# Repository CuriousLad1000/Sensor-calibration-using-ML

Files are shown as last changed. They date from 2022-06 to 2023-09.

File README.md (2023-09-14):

# Sensor calibration using Machine Learning

## Introduction

This repository presents one of the projects I built during the start of
the COVID-19 pandemic when there was a severe shortage of medical
equipment. Even something simple as a thermometer was either not
available or too costly to purchase. In this project, I used some
consumer-grade temperature sensors and calibrated them to provide
medical-grade precision and accuracy.

## Project Objective

The objective is to calibrate a commonly available temperature sensor to
provide medical grade accuracy. The sensor is calibrated by taking
readings from multiple medical grade thermometers as a benchmark and
then averaging them out.

The reading taken from thermometer and the sensor being calibrated are
then fit to a regression model to increase sensor's accuracy.

The model is then uploaded to the controller and after interfacing with
sensors and peripherals required, it produces accurate results under
calibrated range of a clinical thermometer (94-108 degrees F).

*Full list of features and capabilities are listed in a separate section below.*

## Hardware used

-   Arduino nano/pro min

-   3D printer casing for the temperature gun

-   Bright OLED display

-   battery

-   Laser pointer

-   Contactless Temperature sensor

-   Custom-built calibration heat bed

-   Clinical thermometers

-   Precision temperature sensors for heat-bed and reference

## Software used

-   Arduino IDE (C/C++ Programming)

-   Excel for data collection and regression model

-   GIMP for UI designing

-   Eagle for PCB designing

-   Fritzing for prototyping wiring diagram

## Features offered

-   Calibrated contactless temperature sensor.

-   Power-saving mode.

-   Inbuilt rechargeable batteries.

-   Temperature range similar to clinical thermometer.

-   Bright OLED display with easy-to-read readouts.

## Device pics

**Device**

<br/>

<p align="Center">
  
</p>

<br/>
<br/>

**Calibration setup <i>(gotta work with whatever you have during pandemic... this is a makeshift Heatbed PID controlled)</i>**

<br/>

<p align="Center">
  
</p>

<br/>
<br/>

<br/>

<p align="Center">
  
</p>

<br/>
<br/>

**Circuit board**

<br/>

<p align="Center">
  
</p>

<br/>
<br/>

**Calibration process**

<br/>

<p align="Center">
  
</p>

<br/>
<br/>

**UI Testing**

<br/>

<p align="Center">
  
</p>

<br/>
<br/>

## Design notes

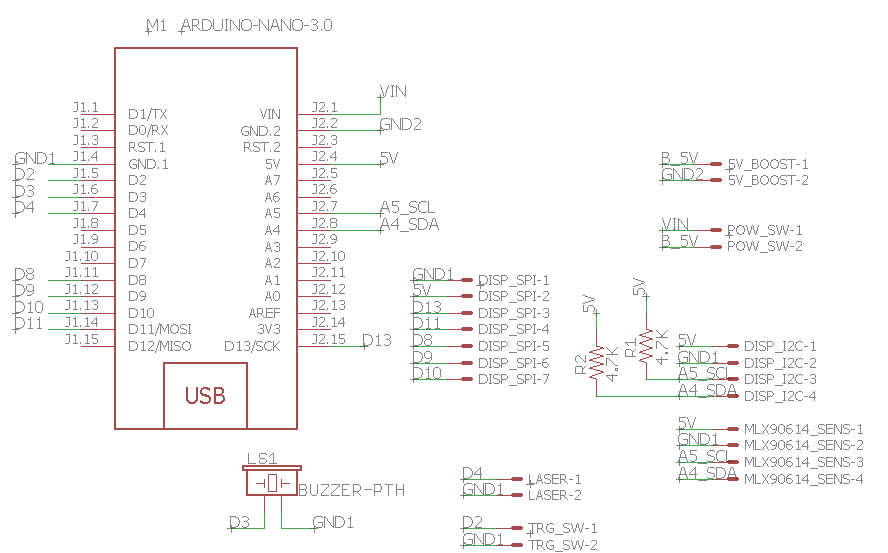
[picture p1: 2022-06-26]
Circuit Schematic/circuit schematic.png

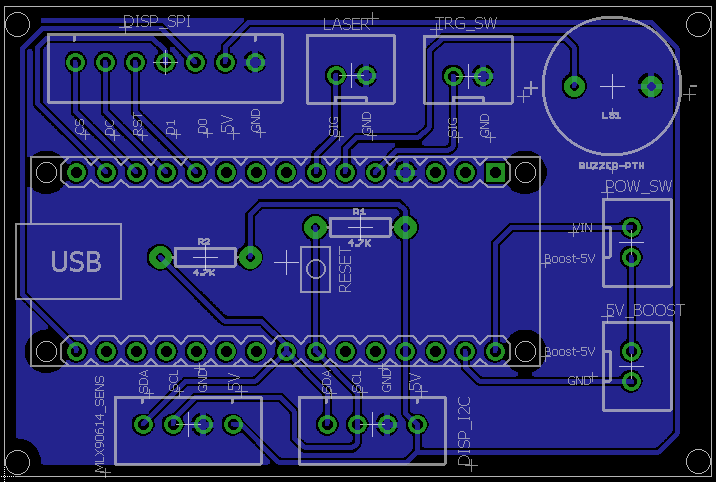
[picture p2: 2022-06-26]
Circuit Schematic/circuit board.png

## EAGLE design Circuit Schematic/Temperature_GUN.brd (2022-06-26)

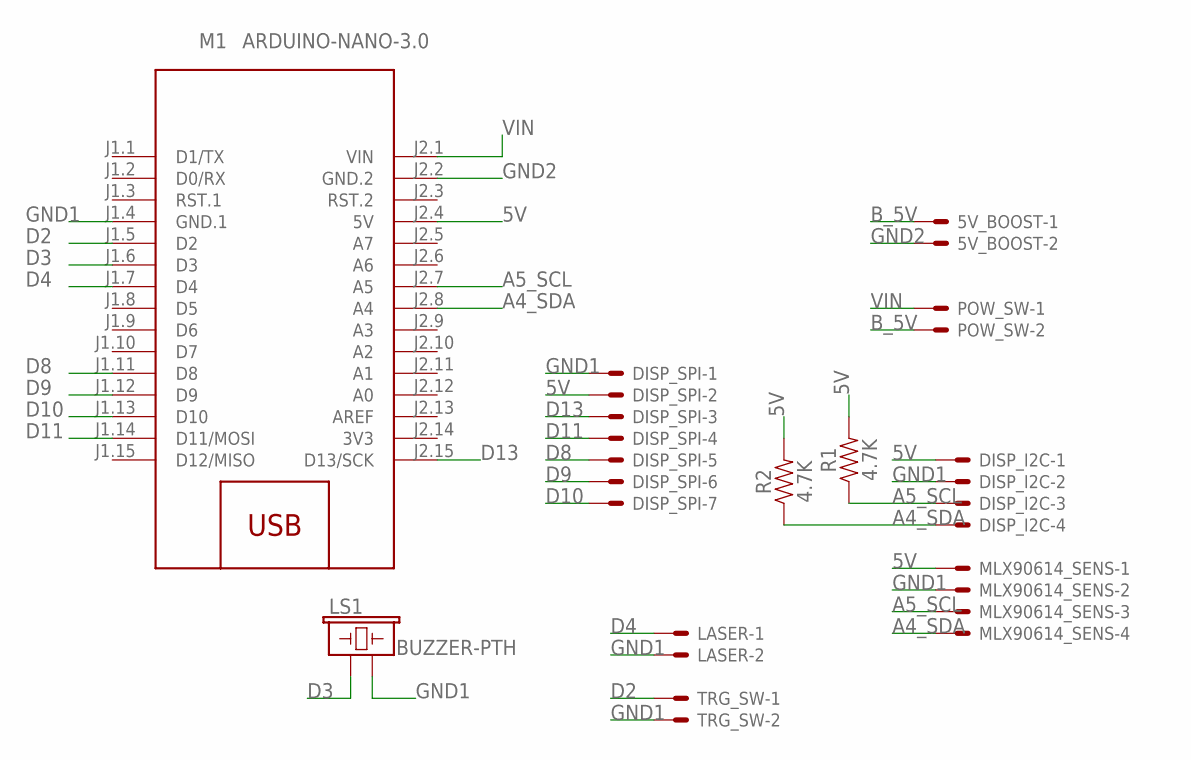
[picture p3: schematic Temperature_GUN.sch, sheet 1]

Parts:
5V_BOOST: JST-XH-02-PIN-ROUND-PAD; JST-XH-02-PACKAGE-ROUND-PAD
DISP_I2C: JST-XH-04-PIN-ROUND-PAD; JST-XH-04-PACKAGE-ROUND-PAD
DISP_SPI: JST-XH-07-PIN-ROUND-PAD; JST-XH-07-PACKAGE-ROUND-PAD
LASER: JST-XH-02-PIN-ROUND-PAD; JST-XH-02-PACKAGE-ROUND-PAD
LS1: BUZZER-PTH; BUZZER-12MM
M1: ARDUINO-NANO-3.0
MLX90614_SENS: JST-XH-04-PIN-ROUND-PAD; JST-XH-04-PACKAGE-ROUND-PAD
POW_SW: JST-XH-02-PIN-ROUND-PAD; JST-XH-02-PACKAGE-ROUND-PAD
R1, R2: 4.7K; AXIAL-0.3
TRG_SW: JST-XH-02-PIN-ROUND-PAD; JST-XH-02-PACKAGE-ROUND-PAD

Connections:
3V3: M1.J2.14 (3V3)
5V: DISP_I2C.1, DISP_SPI.2, M1.J2.4 (5V), MLX90614_SENS.1, R1.P$2 (2), R2.P$2 (2)
A4_SDA: DISP_I2C.4, M1.J2.8 (A4), MLX90614_SENS.4, R2.P$1 (1)
A5_SCL: DISP_I2C.3, M1.J2.7 (A5), MLX90614_SENS.3, R1.P$1 (1)
B_5V: 5V_BOOST.1, POW_SW.2
D2: M1.J1.5 (D2), TRG_SW.1
D3: LS1.+ (1), M1.J1.6 (D3)
D4: LASER.1, M1.J1.7 (D4)
D8: DISP_SPI.5, M1.J1.11 (D8)
D9: DISP_SPI.6, M1.J1.12 (D9)
D10: DISP_SPI.7, M1.J1.13 (D10)
D11: DISP_SPI.4, M1.J1.14 (D11/MOSI)
D13: DISP_SPI.3, M1.J2.15 (D13/SCK)
GND1: DISP_I2C.2, DISP_SPI.1, LASER.2, LS1.- (2), M1.J1.4 (GND.1), MLX90614_SENS.2, TRG_SW.2
GND2: 5V_BOOST.2, M1.J2.2 (GND.2)
VIN: M1.J2.1 (VIN), POW_SW.1

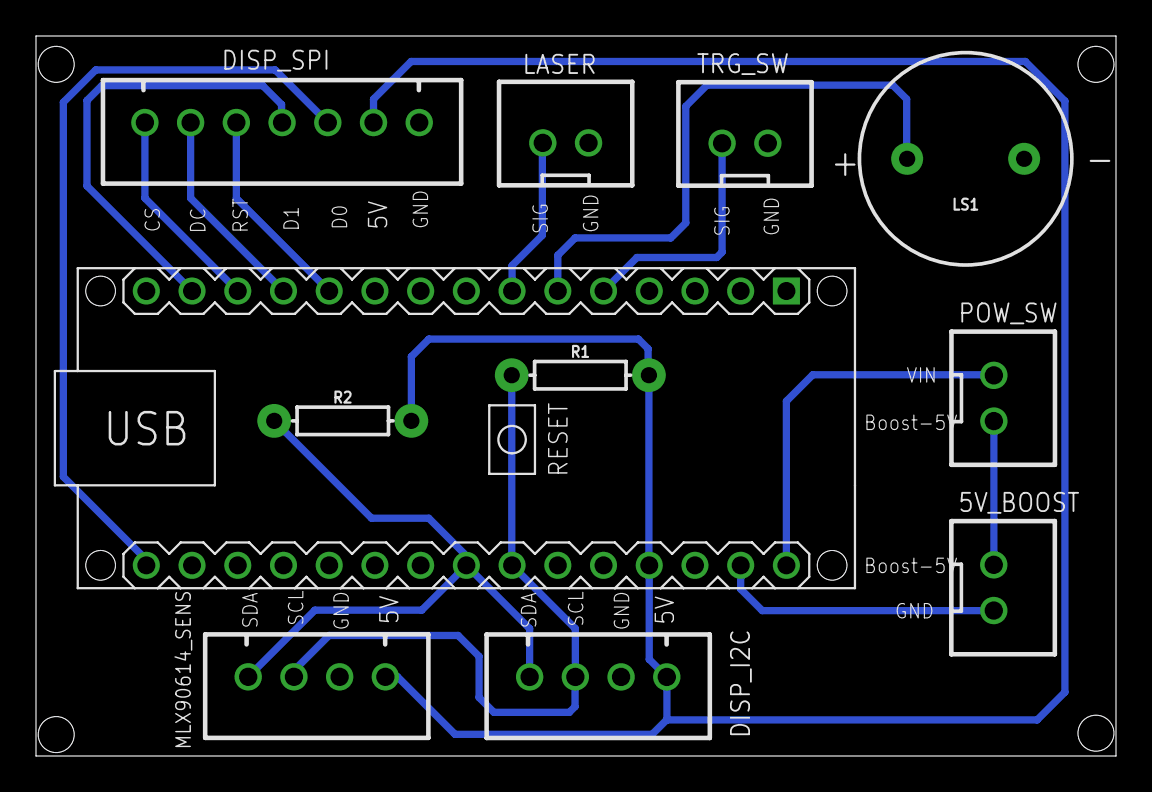
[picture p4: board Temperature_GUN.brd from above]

Board: 2 copper layers, 60.0 x 40.0 mm, 11 parts (0 on the bottom side), 15 nets.

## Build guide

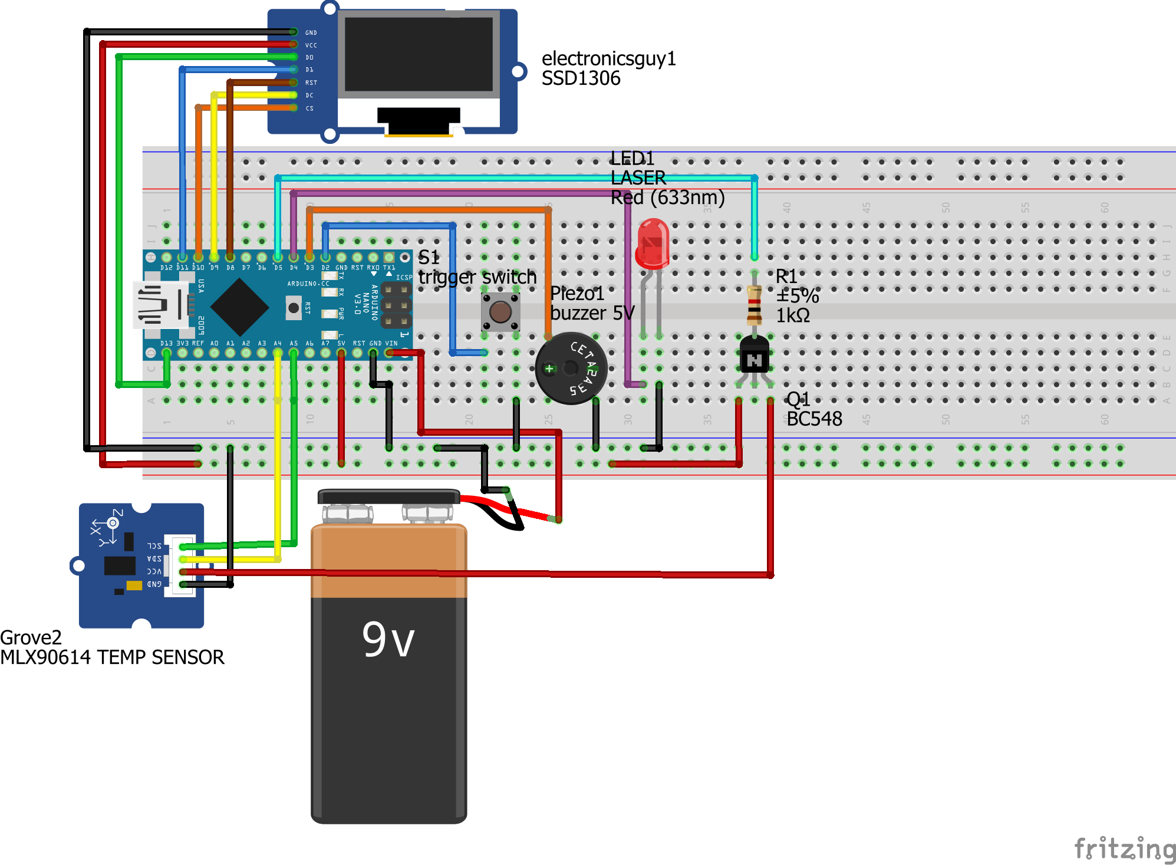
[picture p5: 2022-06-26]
Wiring Diagrams/Temperature_GUN_bb_v6.png

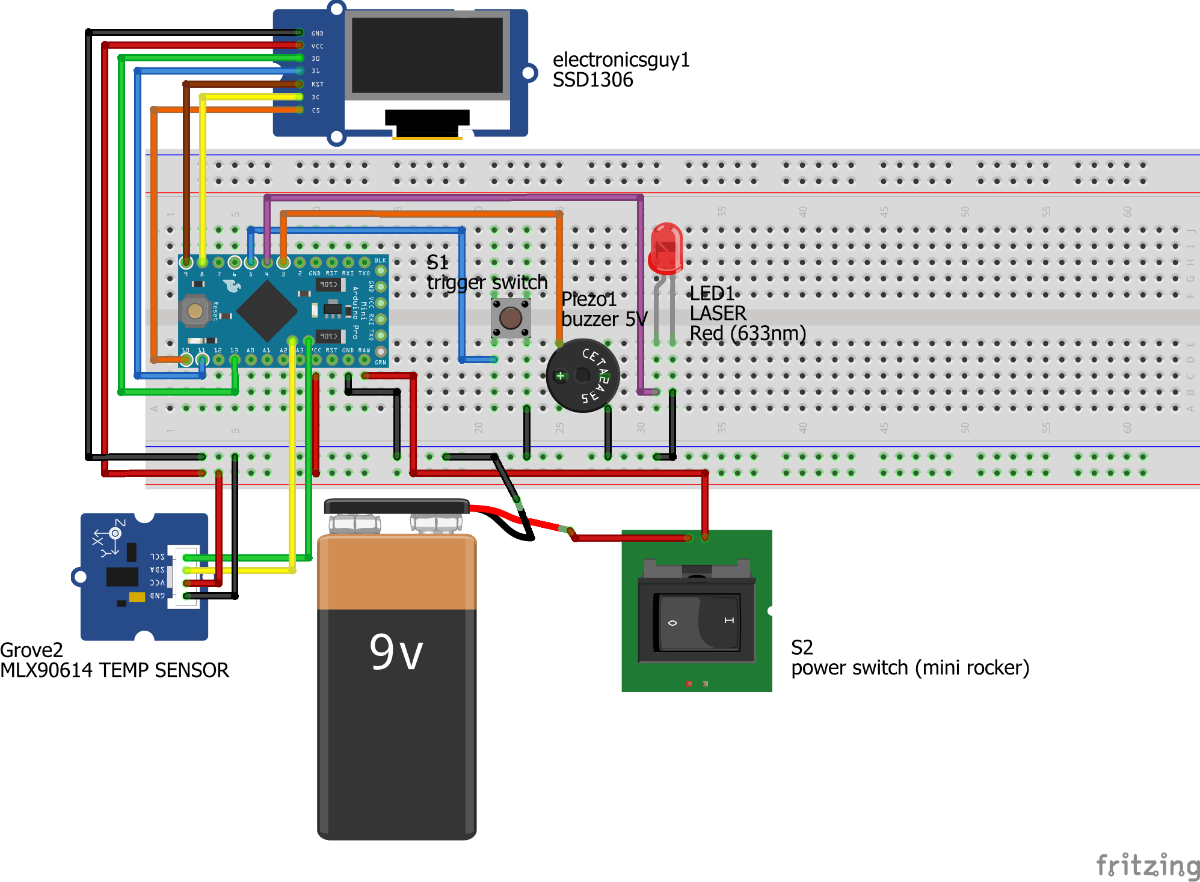
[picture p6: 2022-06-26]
Wiring Diagrams/Temperature_GUN_pro-mini.png

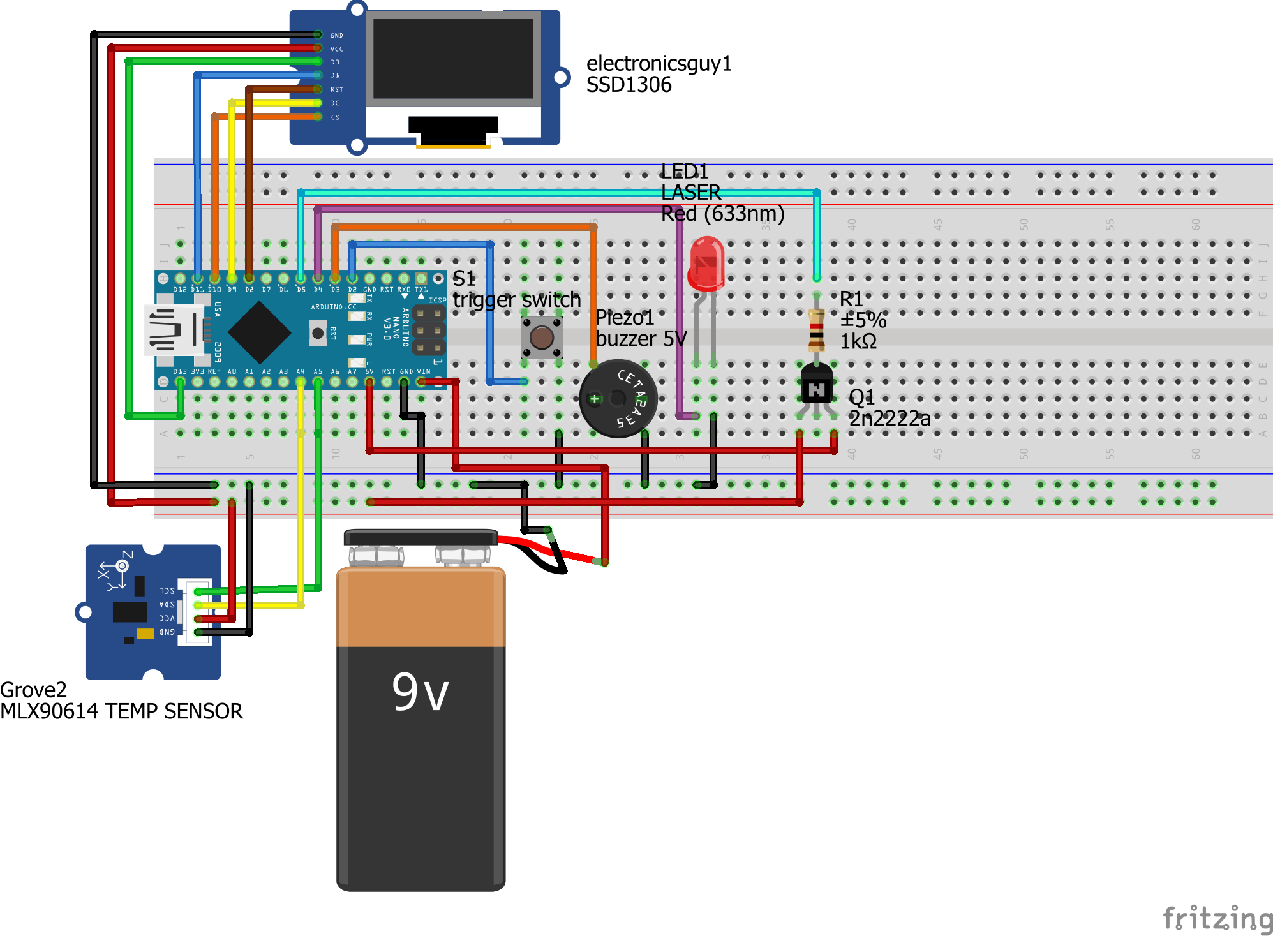
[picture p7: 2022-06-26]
Wiring Diagrams/Temperature_GUN_bb_SingleButton_V5.png

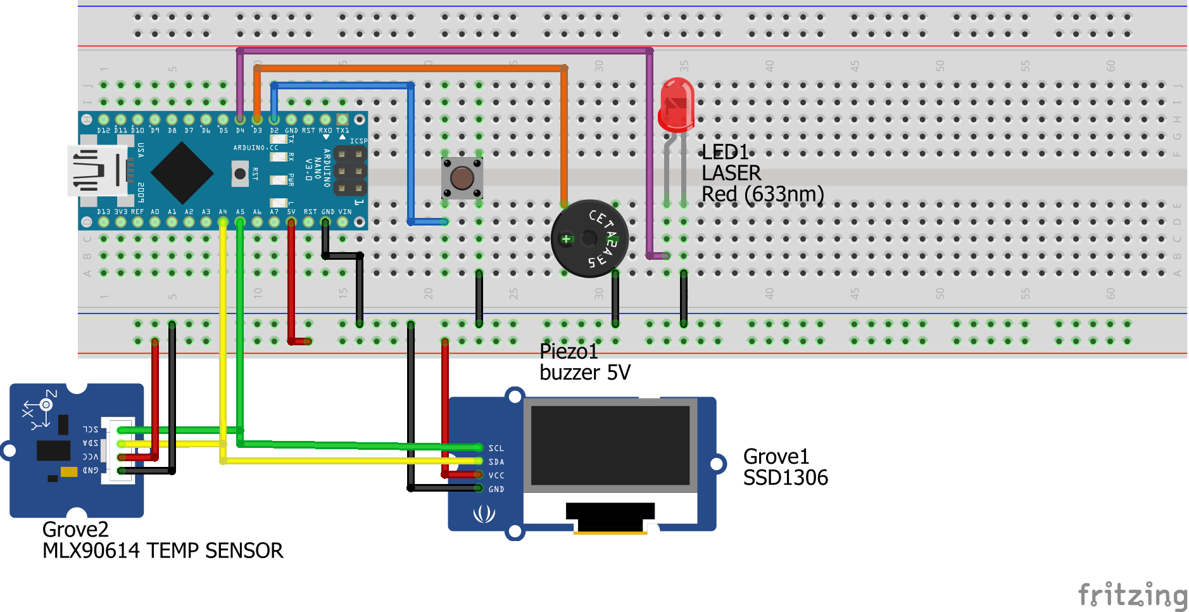
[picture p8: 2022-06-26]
Wiring Diagrams/Temperature_GUN_bb.png

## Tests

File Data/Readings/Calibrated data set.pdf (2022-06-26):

Reference Clinical Thermometer Readout (Y var.) | SET-AVERAGE | Average Regression
Calibrating contactless sensor Readout (2-3 cm) (X var.) | DIFF bw clinical and sensor | Regressed values Calibrating sensor (ŷ = 1.02751X -0.34754) | Diff between Clinical and Regressed Calibrating sensor
Read at (deg F) | Read at (deg F) | Read at (deg F) | Read at (deg F) | Read at (deg F)
94 | 91.57 | 2.43 | 93.74 | 0.26
94.4 | 92.59 | 1.81 | 94.79 | -0.39
94.8 | 93.03 | 1.77 | 95.24 | -0.44
95 | 93.14 | 1.86 | 95.35 | -0.35
95.4 | 93.35 | 2.05 | 95.57 | -0.17
95.8 | 93.59 | 2.21 | 95.81 | -0.01
96 | 93.94 | 2.06 | 96.18 | -0.18
96.4 | 94.20 | 2.20 | 96.45 | -0.05
96.8 | 94.67 | 2.13 | 96.93 | -0.13
97 | 94.65 | 2.35 | 96.90 | 0.10
97.4 | 95.00 | 2.40 | 97.26 | 0.14
97.8 | 95.24 | 2.56 | 97.51 | 0.29
98 | 95.68 | 2.32 | 97.96 | 0.04
98.2 | 95.84 | 2.36 | 98.13 | 0.07
98.4 | 96.08 | 2.32 | 98.38 | 0.02
98.6 | 96.19 | 2.41 | 98.49 | 0.11
98.8 | 96.42 | 2.38 | 98.72 | 0.08
99 | 96.58 | 2.42 | 98.89 | 0.11
99.2 | 96.80 | 2.40 | 99.11 | 0.09
99.4 | 97.04 | 2.36 | 99.37 | 0.03
99.6 | 97.31 | 2.29 | 99.64 | -0.04
99.8 | 97.53 | 2.27 | 99.87 | -0.07
100 | 97.60 | 2.40 | 99.94 | 0.06
100.2 | 97.83 | 2.37 | 100.18 | 0.02
100.4 | 97.93 | 2.47 | 100.28 | 0.12
100.6 | 98.12 | 2.48 | 100.48 | 0.12
100.8 | 98.35 | 2.45 | 100.71 | 0.09
101 | 98.60 | 2.40 | 100.96 | 0.04
101.2 | 98.69 | 2.51 | 101.06 | 0.14
101.4 | 99.05 | 2.35 | 101.43 | -0.03
101.6 | 99.28 | 2.32 | 101.67 | -0.07
101.8 | 99.23 | 2.57 | 101.62 | 0.18
102 | 99.47 | 2.53 | 101.86 | 0.14
102.2 | 99.65 | 2.55 | 102.04 | 0.16
102.4 | 99.85 | 2.55 | 102.25 | 0.15
102.6 | 100.28 | 2.32 | 102.69 | -0.09
102.8 | 100.44 | 2.36 | 102.85 | -0.05
103 | 100.63 | 2.37 | 103.05 | -0.05
103.4 | 100.89 | 2.51 | 103.32 | 0.08
103.8 | 101.14 | 2.66 | 103.58 | 0.22

104 | 101.47 | 2.53 | 103.91 | 0.09
104.4 | 102.02 | 2.38 | 104.48 | -0.08
104.8 | 102.26 | 2.54 | 104.72 | 0.08
105 | 102.55 | 2.45 | 105.02 | -0.02
105.4 | 102.85 | 2.55 | 105.33 | 0.07
105.8 | 103.29 | 2.51 | 105.78 | 0.02
106 | 103.51 | 2.49 | 106.01 | -0.01
106.4 | 104.05 | 2.35 | 106.56 | -0.16
106.8 | 104.27 | 2.53 | 106.79 | 0.01
107 | 104.54 | 2.46 | 107.07 | -0.07
107.4 | 105.03 | 2.37 | 107.57 | -0.17
107.8 | 105.50 | 2.30 | 108.05 | -0.25
108 | 105.66 | 2.34 | 108.22 | -0.22
AVERAGE OFFSET of | 2.36
ŷ = 1.02751X - 0.34754

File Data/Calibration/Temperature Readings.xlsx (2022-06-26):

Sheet: Sheet1
 | Reference Clinical Thermometer Readout | Temperature Gun Readout (2-3cm) | Temperature Difference (clinical and gun) | Lab Thermometer Readout | Lab Thermometer Readout | Temperature Difference (lab and clinical)
Count | Read at (deg F) | Read at (deg F) | Read at (deg F) | Read at (deg F) | Read at (deg C) | Read at (deg F)
0 | 94 | 89.01 | 4.99 | 93.2 | 34 | 0.8
1 | 94.2 | 88.68 | 5.52 | 93.2 | 34 | 1
2 | 94.4 | 88.83 | 5.57 | 93.2 | 34 | 1.2
3 | 94.6 | 88.86 | 5.74 | 93.2 | 34 | 1.4
4 | 94.8 | 88.73 | 6.07 | 93.2 | 34 | 1.6
5 | 95 | 88.92 | 6.08 | 93.2 | 34 | 1.8
6 | 95.2 | 88.94 | 6.26 | 93.2 | 34 | 2
7 | 95.4 | 89.33 | 6.07 | 93.2 | 34 | 2.2
8 | 95.6 | 89.2 | 6.4 | 93.2 | 34 | 2.4
9 | 95.8 | 89.01 | 6.79 | 93.2 | 34 | 2.6
10 | 96 | 89.08 | 6.92 | 93.2 | 34 | 2.8
11 | 96.2 | 88.79 | 7.41 | 93.2 | 34 | 3
12 | 96.4 | 88.4 | 8 | 93.2 | 34 | 3.2
13 | 96.6 | 88.9 | 7.7 | 93.2 | 34 | 3.4
14 | 96.8 | 88.25 | 8.55 | 93.2 | 34 | 3.6
15 | 97 | 89.01 | 7.99 | 93.2 | 34 | 3.8
16 | 97.2 | 88.57 | 8.63 | 93.2 | 34 | 4
17 | 97.4 | 88.83 | 8.57 | 93.2 | 34 | 4.2
18 | 97.6 | 89.4 | 8.2 | 93.2 | 34 | 4.4
19 | 97.8 | 89.12 | 8.68 | 93.2 | 34 | 4.6
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

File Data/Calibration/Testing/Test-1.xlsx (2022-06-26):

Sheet: Sheet2
Reference Clinical Thermometer Readout | Temperature Gun Readout(2-3cm) | Temperature Difference
Read at (deg F) | Read at (deg F) | Read at (deg F)
100.2 | 99.4 | 0.8
100.4 | 99.75 | 0.65
100.6 | 99.83 | 0.77
101.4 | 100.8 | 0.6
101.6 | 100.14 | 1.46
101.8 | 100.99 | 0.81
102 | 101.09 | 0.91
102.2 | 100.41 | 1.79
102.8 | 101.8 | 1
103 | 102.32 | 0.68
103.2 | 102.84 | 0.36
103.4 | 103.53 | -0.13
103.6 | 102.98 | 0.62
103.8 | 102.91 | 0.89
104 | 103.32 | 0.68
104.2 | 103.55 | 0.65
104.4 | 103.43 | 0.97
104.6 | 103.53 | 1.07
105 | 103.9 | 1.1
105.2 | 104.64 | 0.56
105.4 | 105.85 | -0.45
105.6 | 105.99 | -0.39
105.8 | 105.56 | 0.24
106.4 | 106.42 | -0.02
107.2 | 106.77 | 0.43
107.6 | 107.1 | 0.5
107.8 | 107.45 | 0.35
108 | 107.72 | 0.28
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

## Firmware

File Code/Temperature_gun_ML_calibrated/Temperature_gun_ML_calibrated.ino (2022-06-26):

#include <Arduino.h>
#include <U8g2lib.h>
#include <SparkFunMLX90614.h> // SparkFunMLX90614 Arduino library
#include <Wire.h>
//#include <movingAvg.h>



#define MSG_DEBUG
#define home_page_width 128
#define home_page_height 64

#define normal_tempF_max  99.5
#define mild_tempF_max    101


//#define MovReadings 10
#define avgReadings 8

//amb. temp >83 & < 91  avg offset 3.23

#define m1   1.02751
#define c1  -0.34754

//amb. temp >91  avg offset 3.23
#define m2   1.03983
#define c2  -0.66635

U8G2_SSD1306_128X64_NONAME_1_4W_HW_SPI u8g2(U8G2_R0, /* cs=*/ 10, /* dc=*/ 9, /* reset=*/ 8);

IRTherm therm; // Create an IRTherm object to interact with throughout
//movingAvg TEMP(MovReadings);

static const unsigned char splash_120x63_bits[] U8X8_PROGMEM = {
  //enter here splash screen .xbm code
};

static const unsigned char welcome_120x36_bits[] U8X8_PROGMEM = {
  //enter here welcome screen .xbm code
};

static const unsigned char cool_28x28_bits[] U8X8_PROGMEM = {
  0x00, 0x00, 0x00, 0x00, 0x00, 0x60, 0x00, 0x00, 0x00, 0x64, 0x02, 0x00,
  0x00, 0x68, 0x01, 0x00, 0x00, 0xf0, 0x00, 0x00, 0x40, 0x60, 0x20, 0x00,
  0x40, 0x60, 0x20, 0x00, 0x4c, 0x60, 0x20, 0x03, 0x78, 0x60, 0xe0, 0x01,
  0xe0, 0x60, 0x70, 0x00, 0xf8, 0x61, 0xf8, 0x01, 0x0c, 0x66, 0x06, 0x03,
  0x00, 0xfc, 0x03, 0x00, 0x00, 0xf0, 0x00, 0x00, 0x00, 0xf0, 0x00, 0x00,
  0x00, 0x7c, 0x03, 0x00, 0x0c, 0x66, 0x06, 0x03, 0xf8, 0x61, 0xf8, 0x01,
  0xe0, 0x60, 0x70, 0x00, 0x78, 0x60, 0xe0, 0x01, 0x4c, 0x60, 0x20, 0x03,
  0x40, 0x60, 0x20, 0x00, 0x60, 0x60, 0x60, 0x00, 0x00, 0xf0, 0x00, 0x00,
  0x00, 0x68, 0x01, 0x00, 0x00, 0x64, 0x02, 0x00, 0x00, 0x60, 0x00, 0x00,
  0x00, 0x00, 0x00, 0x00
};

static const unsigned char hot_28x28_bits[] U8X8_PROGMEM = {
  0x00, 0x10, 0x00, 0x00, 0x00, 0x70, 0x00, 0x00, 0x00, 0xc8, 0x00, 0x00,
  0x00, 0x88, 0x01, 0x00, 0x00, 0x08, 0x03, 0x00, 0x00, 0x04, 0x04, 0x00,
  0x00, 0x06, 0x08, 0x00, 0x00, 0x02, 0x10, 0x00, 0x00, 0x01, 0x30, 0x00,
  0x80, 0xc0, 0x60, 0x00, 0xc0, 0xc0, 0x41, 0x00, 0x60, 0x40, 0x81, 0x00,
  0x20, 0x40, 0x82, 0x00, 0x10, 0x40, 0x06, 0x01, 0x18, 0x40, 0x04, 0x01,
  0x08, 0x46, 0x04, 0x01, 0x08, 0x6e, 0x08, 0x03, 0x0c, 0x31, 0x08, 0x02,
  0x04, 0x01, 0x08, 0x02, 0x04, 0x01, 0x0c, 0x02, 0x04, 0x01, 0x04, 0x01,
  0x08, 0x03, 0x04, 0x01, 0x08, 0x06, 0x02, 0x01, 0x18, 0x00, 0x80, 0x00,
  0x30, 0x00, 0xc0, 0x00, 0x60, 0x00, 0x60, 0x00, 0xc0, 0x01, 0x30, 0x00,
  0x00, 0x07, 0x18, 0x00
};

static const unsigned char warm_28x28_bits[] U8X8_PROGMEM = {
  0x18, 0x30, 0x60, 0x00, 0x78, 0xf0, 0xe0, 0x01, 0x18, 0x30, 0x70, 0x00,
  0x24, 0x68, 0xd0, 0x00, 0x20, 0x40, 0x80, 0x00, 0x40, 0xc0, 0x80, 0x01,
  0x40, 0x80, 0x00, 0x01, 0x40, 0x80, 0x00, 0x01, 0x40, 0x80, 0x00, 0x01,
  0x40, 0x80, 0x00, 0x01, 0x20, 0x40, 0x80, 0x00, 0x20, 0x40, 0x80, 0x00,
  0x30, 0x20, 0x40, 0x00, 0x10, 0x20, 0x40, 0x00, 0x10, 0x20, 0x40, 0x00,
  0x10, 0x20, 0x40, 0x00, 0x30, 0x60, 0xc0, 0x00, 0x20, 0x40, 0x80, 0x00,
  0x60, 0xc0, 0x80, 0x01, 0x40, 0x80, 0x00, 0x01, 0x40, 0x80, 0x00, 0x01,
  0x40, 0x80, 0x00, 0x01, 0x40, 0x80, 0x00, 0x01, 0x60, 0xc0, 0x80, 0x00,
  0x20, 0x40, 0x80, 0x00, 0x30, 0x20, 0x40, 0x00, 0x10, 0x20, 0x40, 0x00,
  0x18, 0x10, 0x20, 0x00
};

#define buzz_pin 3
#define laser_pin 4

const byte LED_PIN = 8; // Optional LED attached to pin 8 (active low)

//float newEmissivity = 0.97;
//float newEmissivity = 0.95;
float Temp_Celcius;
float Temp_Farenheit;
float Temp_AmbientF;

void setup()
{
  therm.begin(); // Initialize thermal IR sensor
  therm.setUnit(TEMP_F); // Set the library's units to Farenheit
  //therm.setUnit(TEMP_C); // Set the library's units to Farenheit
  //therm.setEmissivity(newEmissivity);
  pinMode(buzz_pin, OUTPUT);
  pinMode(laser_pin, OUTPUT);
#ifdef MSG_DEBUG
  Serial.begin(115200);
#endif

  u8g2.begin();
  disp_splash();
  //TEMP.begin();

  Serial.println("======================== START =============================");

  Serial.print("Emissivity set at: ");
  Serial.print(therm.readEmissivity());

  therm.readRange();//Read minimum and maximum ranges of temperature set in sensor's eeprom
  Serial.print(" Min T: ");
  Serial.print(therm.minimum());
  Serial.print(" Max T: ");
  Serial.println(therm.maximum());

}

float readTEMP()
{
  float AVGread = 0;
  Temp_AmbientF = 0;
  float Regr_Read = 0;
  for (int i = 1; i <= avgReadings; i++)
  {
    if (therm.read()) // On success, read() will return 1, on fail 0.
    {
      AVGread = AVGread + therm.object();
      Temp_AmbientF = Temp_AmbientF + therm.ambient();
    }
    else
      return -1;
    delay(120);
  }
  AVGread = AVGread / avgReadings;
  Temp_AmbientF = Temp_AmbientF / avgReadings;

  if (Temp_AmbientF < 92)
  {
    Regr_Read = (m1 * AVGread) + c1; //Add Primary Linear Regression model here... anbient temp is between 83 to 90 F when temp. rises from 94 to 108
  }
  else
  {
    Regr_Read = (m2 * AVGread) + c2; //Add Secondary model here... 
  }

#ifdef MSG_DEBUG
  Serial.print("Cal. Temp.: ");
  Serial.print(Regr_Read);
  Serial.print("   Average Temp.: ");
  Serial.print(AVGread);
  Serial.print("   Ambient Temp.: ");
  Serial.print(Temp_AmbientF);
  Serial.println(" F ");

#endif

  return Regr_Read; //values without corrections added to it
}


void loop()
{
  //delay(500);
  //idle_UI();
  //delay(500);
  //digitalWrite(laser_pin, HIGH);

  //Temp_Farenheit = Move_TEMP();
  Temp_Farenheit = readTEMP();

  //Temp_Celcius = (Temp_Farenheit - 32) * .5556;

  if (Temp_Farenheit <= normal_tempF_max) //Temp less than 99.6 temperature is normal
  {
    UI(Temp_Farenheit, Temp_Celcius, 0); //normal
    //beep(0);
  }
  else if ((Temp_Farenheit > normal_tempF_max) && (Temp_Farenheit <= mild_tempF_max)) //temp between 99.6 and 101 then  mild fever
  {
    UI(Temp_Farenheit, Temp_Celcius, 1); //MILD Fever
    //beep(1);
  }
  else if (Temp_Farenheit > mild_tempF_max) //temp greater than 101.00 then high fever
  {
    UI(Temp_Farenheit, Temp_Celcius, 2); //HIGH Fever
    //beep(2);
  }
  delay(500);
  //while (1);
}


void UI(float TF, float TC, uint8_t flag)
{
  u8g2.firstPage();
  do
  {
    u8g2.drawFrame(0,  0,  home_page_width,  home_page_height);
    u8g2.drawHLine(0, 45, 128);
    u8g2.drawVLine(92, 0, 45);

    u8g2.setFont(u8g2_font_luIS14_tf);  //u8g2_font_luIS14_tr  u8g2_font_fur14_tf  u8g2_font_ncenB14_tr
    u8g2.setCursor(0, 18);
    u8g2.print(TF);
    u8g2.setCursor(0, 40);
    u8g2.print(TC);
    u8g2.drawGlyph(70, 18, 0x00b0);
    u8g2.drawGlyph(70, 40, 0x00b0);
    u8g2.setFont(u8g2_font_luIS12_tr);  //u8g2_font_luIS14_tr  u8g2_font_fur14_tf  u8g2_font_ncenB14_tr
    u8g2.drawStr(75, 18, "F");
    u8g2.drawStr(75, 40, "A");
    //u8g2.drawStr(75, 40, "C");

    if (flag == 0)
    {
      u8g2.drawStr(3, 60, "NORMAL");
      u8g2.drawXBMP(96, 8, 28, 28, cool_28x28_bits);
    }
    else if (flag == 1)
    {
      u8g2.drawStr(3, 60, "MILD FEVER");
      u8g2.drawXBMP(96, 8, 28, 28, warm_28x28_bits);
    }
    else if (flag == 2)
    {
      u8g2.drawStr(3, 60, "HIGH FEVER");
      u8g2.drawXBMP(96, 8, 28, 28, hot_28x28_bits);
    }
    else if (flag == 3)
    {
      u8g2.drawStr(3, 60, "ERROR");
    }
  } while ( u8g2.nextPage()); //will print data to screen until it turns false
}

void disp_splash()
{
  u8g2.firstPage();
  do
  {
    u8g2.drawXBMP(3, 1, 120, 63, splash_120x63_bits);
  } while ( u8g2.nextPage()); //will print data to screen until it turns false
}

void beep(uint8_t flag)
{
  if (flag == 0)
  {
    for (int i = 0; i < 2; i++)
    {
      digitalWrite(buzz_pin, HIGH);
      delay(50);
      digitalWrite(buzz_pin, LOW);
      delay(50);
    }
  }
  else if (flag == 1)
  {
    for (int i = 0; i < 3; i++)
    {
      digitalWrite(buzz_pin, HIGH);
      delay(100);
      digitalWrite(buzz_pin, LOW);
      delay(100);
    }
  }
  else if (flag == 2)
  {
    for (int i = 0; i < 5; i++)
    {
      digitalWrite(buzz_pin, HIGH);
      delay(500);
      digitalWrite(buzz_pin, LOW);
      delay(500);
    }
  }
}

void idle_UI()
{
  u8g2.firstPage();
  do
  {
    u8g2.drawFrame(0,  0,  home_page_width,  home_page_height);
    u8g2.drawHLine(0, 45, 128);
    u8g2.drawVLine(92, 0, 45);

    u8g2.setFont(u8g2_font_luIS14_tf);  //u8g2_font_luIS14_tr  u8g2_font_fur14_tf  u8g2_font_ncenB14_tr
    u8g2.setCursor(0, 18);
    u8g2.print("___.__");
    u8g2.setCursor(0, 40);
    u8g2.print("___.__");
    u8g2.drawGlyph(70, 18, 0x00b0);
    u8g2.drawGlyph(70, 40, 0x00b0);

    u8g2.setFont(u8g2_font_luIS12_tr);  //u8g2_font_luIS14_tr  u8g2_font_fur14_tf  u8g2_font_ncenB14_tr
    u8g2.drawStr(75, 18, "F");
    u8g2.drawStr(75, 40, "C");
    u8g2.drawStr(3, 60, "Press Trigger");

  } while ( u8g2.nextPage()); //will print data to screen until it turns false
}

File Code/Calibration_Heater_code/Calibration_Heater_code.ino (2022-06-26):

//#include <PreciseLM35.h>
#include "OneButton.h"
#include <OneWire.h>
#include <DallasTemperature.h>
//#include <PID_v1.h>

OneButton button(3, true);


#define avgReadings 50
#define pinLM35 A1
#define Temp_sens_pin 6    //declare a variable to store Temperature sensor pin value
#define buzz 7
#define pot A0
#define PWM_Heater_PIN 10
int dat;

unsigned long lastMilliPrint = 0;
double Setpoint_Temp, Actual_Temp, Output_Heater_PWM, Temp;
const float measuredVsReadArefRatio = 0.9936; // enter here your ratio between measured and expected AREF
bool flag;

//double Kp = 1.5, Ki = 2.5, Kd = 4.5; //Specify the links and initial tuning parameters

//PreciseLM35 lm35(pinLM35, INTERNAL, measuredVsReadArefRatio);
OneWire  oneWire(Temp_sens_pin); //create an instance to use OneWire library
DallasTemperature sensors(&oneWire); // Create an instance to use DallasTemperature library
//PID myPID(&Actual_Temp, &Output_Heater_PWM, &Setpoint_Temp, Kp, Ki, Kd, DIRECT);


float Read = 0;
float DS_TMP = 0;

void setup()
{

  //Actual_Temp = lm35.readCelsius();
  pinMode(buzz, OUTPUT);

  Setpoint_Temp = 94.0;  //Temp. to reach
  Serial.begin(115200);
  button.attachDoubleClick(doubleclick);
  button.attachClick(clik);
  pinMode(PWM_Heater_PIN, OUTPUT);
  sensors.begin();

//  myPID.SetMode(AUTOMATIC);  //turn the PID on
}

void loop()
{
  //button.tick();
  dat = analogRead(pot);

  //Serial.print("Pot: ");
  //Serial.print(dat);

  dat = map(dat, 0, 1023, 0, 255);
  analogWrite(PWM_Heater_PIN, dat);

  //Temp = lm35.readCelsius();
  //  Temp = AVG_TEMP();
  //  Actual_Temp = Temp;

  do
  {
    sensors.requestTemperatures(); // Send the command to get temperatures
    //DS_TMP = sensors.getTempCByIndex(0); // You can have more than one IC on the same bus.  // 0 refers to the first IC on the wire
    DS_TMP = sensors.getTempFByIndex(0); // You can have more than one IC on the same bus.  // 0 refers to the first IC on the wire
  } while (DS_TMP == -196.60);

  Temp = DS_TMP;
  Actual_Temp = Temp;

  // Serial.print(" Glass_temp(C): ");
  // Serial.print(DS_TMP);

  //Serial.println();

 // myPID.Compute();
  //analogWrite(PWM_Heater_PIN, Output_Heater_PWM);
  printTempInfo();    // display data
}



float AVG_TEMP()
{
  float AVGread = 0;

  for (int i = 0; i < avgReadings; i++)
  {
    button.tick();
    //AVGread = AVGread + lm35.readCelsius();
    //AVGread = AVGread + lm35.readFahrenheit();
    delay(10);
  }
  AVGread = AVGread / avgReadings;
  return AVGread;
}


void printTempInfo()
{ // display data
  if ((millis() - lastMilliPrint) >= 150)
  {
    lastMilliPrint = millis();
    Serial.print("Water_Temp.:");
    Serial.print(Temp);   // CURRENT Temp. APPROACHING SETPOINT
  //  Serial.print(", SP:");
   // Serial.print(Setpoint_Temp); //SETPOINT LEFT
    //Serial.print(", DIFF:");
   // Serial.print(Setpoint_Temp - Temp); // CURRENT Temp. APPROACHING SETPOINT

    Serial.print(",   PWM:");
    //Serial.print(Output_Heater_PWM);   // PWM VALUE
    Serial.print(dat);   // PWM VALUE

    // Serial.print(",");
    // Serial.print(DS_TMP);  //DS_18b20_Temp
    // Serial.print(",");
    // Serial.print(Output_Heater_PWM);   // PWM VALUE

    Serial.println();

    /*  if (Setpoint_Temp - Temp <= 0.2 && (Setpoint_Temp - Temp > -0.2))
      {
        flag = 1;
        beep();
      }
      else
        flag = 0;
      beep();  */
  }

}

void beep()
{
  if (flag == 1)
  {
    digitalWrite(buzz, HIGH);
    //flag = 0;
  }
  else
  {
    digitalWrite(buzz, LOW);
    //flag = 1;
  }

}


void doubleclick()
{
  Setpoint_Temp = Setpoint_Temp - 0.20; //Temp. to reach
} // doubleclick

void clik()
{
  Setpoint_Temp = Setpoint_Temp + 0.20; //Temp. to reach
} //click

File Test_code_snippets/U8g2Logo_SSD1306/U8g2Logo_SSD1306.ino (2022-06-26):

/*

  U8g2Logo.ino

  Universal 8bit Graphics Library (https://github.com/olikraus/u8g2/)

  Copyright (c) 2016, olikraus@gmail.com
  All rights reserved.

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
  THIS SOFTWARE IS PROVIDED BY THE COPYRIGHT HOLDERS AND
  CONTRIBUTORS "AS IS" AND ANY EXPRESS OR IMPLIED WARRANTIES,
  INCLUDING, BUT NOT LIMITED TO, THE IMPLIED WARRANTIES OF
  MERCHANTABILITY AND FITNESS FOR A PARTICULAR PURPOSE ARE
  DISCLAIMED. IN NO EVENT SHALL THE COPYRIGHT HOLDER OR
  CONTRIBUTORS BE LIABLE FOR ANY DIRECT, INDIRECT, INCIDENTAL,
  SPECIAL, EXEMPLARY, OR CONSEQUENTIAL DAMAGES (INCLUDING, BUT
  NOT LIMITED TO, PROCUREMENT OF SUBSTITUTE GOODS OR SERVICES;
  LOSS OF USE, DATA, OR PROFITS; OR BUSINESS INTERRUPTION) HOWEVER
  CAUSED AND ON ANY THEORY OF LIABILITY, WHETHER IN CONTRACT,
  STRICT LIABILITY, OR TORT (INCLUDING NEGLIGENCE OR OTHERWISE)
  ARISING IN ANY WAY OUT OF THE USE OF THIS SOFTWARE, EVEN IF
  ADVISED OF THE POSSIBILITY OF SUCH DAMAGE.

*/

#include <Arduino.h>
#include <U8g2lib.h>

#ifdef U8X8_HAVE_HW_SPI
#include <SPI.h>
#endif
#ifdef U8X8_HAVE_HW_I2C
#include <Wire.h>
#endif

/*
  U8g2lib Example Overview:
    Frame Buffer Examples: clearBuffer/sendBuffer. Fast, but may not work with all Arduino boards because of RAM consumption
    Page Buffer Examples: firstPage/nextPage. Less RAM usage, should work with all Arduino boards.
    U8x8 Text Only Example: No RAM usage, direct communication with display controller. No graphics, 8x8 Text only.

  This is a page buffer example.
*/
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

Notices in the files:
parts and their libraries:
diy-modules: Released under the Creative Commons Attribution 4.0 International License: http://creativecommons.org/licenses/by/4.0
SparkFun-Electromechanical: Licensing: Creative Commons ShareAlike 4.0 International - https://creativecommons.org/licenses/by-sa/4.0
